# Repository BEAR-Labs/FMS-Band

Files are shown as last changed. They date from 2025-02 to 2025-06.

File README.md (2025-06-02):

## FMS Band
> [!WARNING]  
> **This page is still under construction**

## Introduction
Hand gesture recognition is a vital component in the development of technologies such as prosthetics, exoskeletons, and virtual reality systems, offering intuitive and user-friendly control interfaces. However, the high cost of production, including expensive commercial software, create barriers to their accessibility, particularly for research and clinical cases. The armband design focuses on fitment for consistent sensor contact, accessibility through affordable components and open-source tools, and modularity for customization and integration with various systems. This manual aims to guide the process of constructing a low-cost, open-source Force Myography (FMG) device.

### FMG
This design uses FMG technology to detect radial muscle forces on the forearm, capturing patterns from hand gestures. The process relies on sensors picking up measurements that reflect the muscle activity that are later analyzed offline using a linear discriminant analysis (LDA) classifier to correlate the FMG (voltage) data with each hand gesture.

## Materials
| Item | Quantity | Cost Per Unit | Total Cost |
|------|----------|----------------|------------|
| FSR400 | 8 | $2.99 | $23.92 |
| Velcro Strap | 1 | $8.49 | $8.49 |
| Velcro Adhesive Tape | 1 | $8.99 | $8.99 |
| 30 AWG Flexible Cable | 1 | $12.99 | $12.99 |
| PCB Protoboard (×20) | 1 | $9.99 | $9.99 |
| ABS Resin | 1 | $44.09 | $44.09 |
| Copper Tape | 1 | $6.88 | $6.88 |
| PDMS Domes (x100) | 1 | $7.99 | $7.99 |
| 7.5 kOhm Resistors (x100) | 1 | $5.49 | $5.49 |
| Wiring Sheath | 1 | $7.63 | $7.63 |
| Hot Glue Sticks (x10) | 1 | $2.92 | $2.92 |
| Solder | 1 | $5.79 | $5.79 |
| Dupont Connectors | 1 | $12.99 | $12.99 |
| **Total Cost** | | | **$162.60** |

## Cradle/Sensor Design
The FMG band’s core components include FSR400 sensors integrated into a voltage divider which converts the resistance of the FSRs into measurable voltage signals based on the force applied. The mechanical design consists of 3D-printed resin cradles to hold the FSRs in place, adhesive polydimethylsiloxane (PDMS) domes for even force distribution (seen mounted on the sensors), and a Velcro strap for adjustability. The modular design allows for easy sensor replacement or integration of additional components as needed.



> PDMS Dome, FSR400, and Sensor Cradle

### Cradle Construction

1. Print eight cradles using the `Real_Holder_V9.stl` provided.  
   > *Image to be added*

2. Place an FSR400 pressure sensor into each cradle and use super glue to secure the sensor in position.  
   > *Image to be added*

3. Carefully fit a PDMS dome to the sensing surface of each FSR, making sure there is full coverage over the active sensing region.  
   > *Image to be added*

4. Bend the FSR solder tabs at a 90° angle so they lay flat on the cradle.  
   > *Image to be added*

5. Solder the input and output wires to the solder tabs, and secure the connections with a thin layer of hot glue.
   > *Image to be added*

6. Mount the completed sensor units onto a Velcro base band for easy adjustment and modularity.  
   > *Image to be added*

## Circuit Design - Voltage Divider (VD)
Each FSR400 sensor is placed externally on the Velcro armband and connected to the circuit board through dedicated pin headers. One pin of the FSR is connected to an external +5V source, while the other pins are connected to a junction on the circuit board. In this junction, one end is linked to the 7.5 kΩ resistor and another to an output signal device, Sig0. The end of the resistor not connected to the pin junction is connected to GND. Sig0 is measured at the junction between the FSR and resistor and is sent to an external microcontroller through another set of dedicated pins.



> Single VD channel replicated 8 times across the board for each sensor

### Assembling the VD Circuit

1. Solder pin headers for Sig0, FSR400, GND, 5V onto the protoboard.




2. Solder 7.5 kΩ resistors to the protoboard, leaving space between the resistors and the pin headers. Connect one end of each 7.5 kΩ resistor together to form a junction, then solder one end of that junction to GND.  

   
   

3. Create a junction between the resistors and the FSR400 leaving space for another wire to come in.

 
 

4. Create a junction between the FSR400 pin header, the Sig0 pin header, and the free end of a 7.5 kΩ resistor. One end of the wire should be in the junction while the other end should connect to the Sig0 pin header.

 
 

5. Connect one pin of the FSR400 header to +5V and one pin of the Sig0 header to GND.




6. Complete!
   


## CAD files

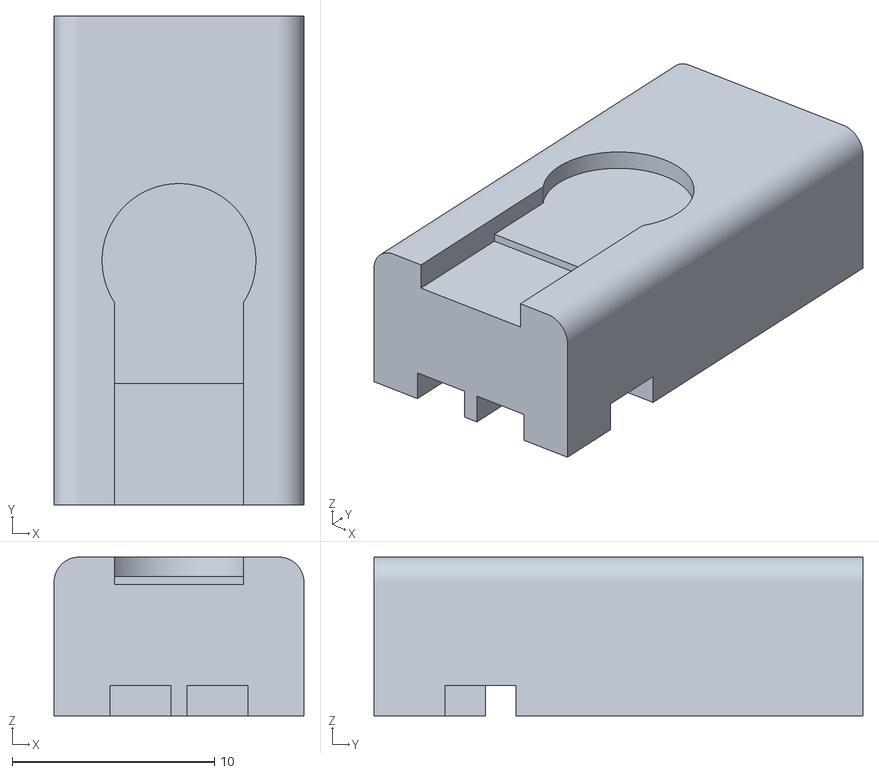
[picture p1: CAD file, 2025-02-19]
Real_holder_V9.stl
12.4 x 24.1 x 7.85

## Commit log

2025-02-19 Started README.md
    Added Introduction and Materials to FMS Band Repository
2025-02-19 Added Cradle STL
    [Real_holder_V9.stl]
